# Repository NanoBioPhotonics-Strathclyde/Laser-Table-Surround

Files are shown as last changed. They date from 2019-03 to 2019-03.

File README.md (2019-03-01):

# Laser Table Surround

This project details the laser safety enclosure we have constructed for use with a 3x1.5m optical table. Wtih simple modifications it can be used for other sized tables.
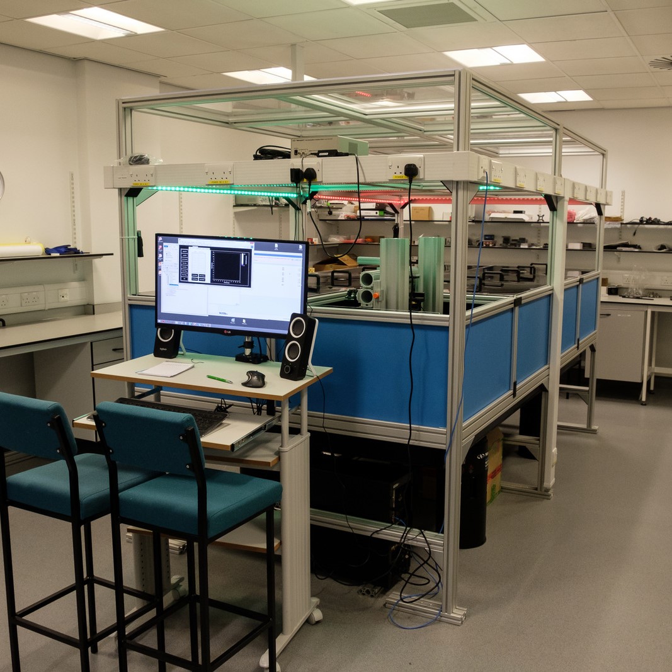
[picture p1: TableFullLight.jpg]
Laser Surround Table Fully Lit

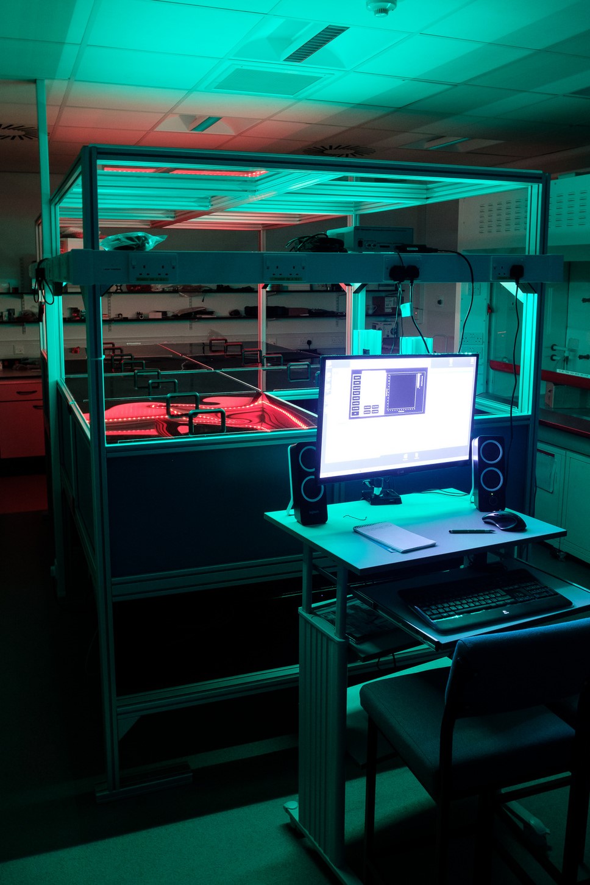
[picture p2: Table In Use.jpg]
Laser Surround in use

There were some key design considerations:
* Easily customised for other tables
* Use standard materials available from multiple suppliers when possible
* Use low cost shelving so that it can be modified quickly and replaced easily if necessary
* Stand free of the table to minimise vibration when removing top access panels
* Allow removal of side panels when necessary, but not in a way to make too easy (to prevent routine disabling of a key safety feature)
* Allow variable height from table to upper covers. This can be changed as required (though will take some disassembly).

On the last point - our optical setup means that the default height on the covers requires some lab members to use steps when accessing parts of the table. We recommend thinking about what height your sides actually need to be placed at!

The file TableSurroundConstructionHelp.pdf provides a construction schematic, and the original Sketchup design file is TableWithSurround.skp. Note that this is in multiple layers containing different classes of components. The colour coding identifies identical parts (by length or type)

We settled on aluminium extrusion for the frame. There are a number of suppliers; we used "Item 8" and the parts numbers in the full parts spreadsheet ("TableSurround Parts Sheet.ods") refer to the catalogue at:
https://www.item24.de/en/productworld/building-kit-system/item-profiles.html

The file "PanelHolderCutList.txt" gives a sample cut list to generate the required lengths from standard 2m lengths  of the profile.

We used 2mm black anodised aluminium for the side panels and sprayed the outer sides with self-priming acrylic for aesthetic purposes.

We then used 10mm clear plexiglass (any supplier) for the shelving and dark 5mm plexiglass with handles from rs for the covers. Clear plexiglass is useful for the shelving as it is strong, easily cut, and allows room light to the table when not working in the dark. The dark plexiglass for the covers was chosen as we enclose the beam paths on our table, so the covers are working to provide thermal stability and prevent room light ingress rather than as the primary safety mechanism for beams travelling vertically. Use alternative materials when this is the case.
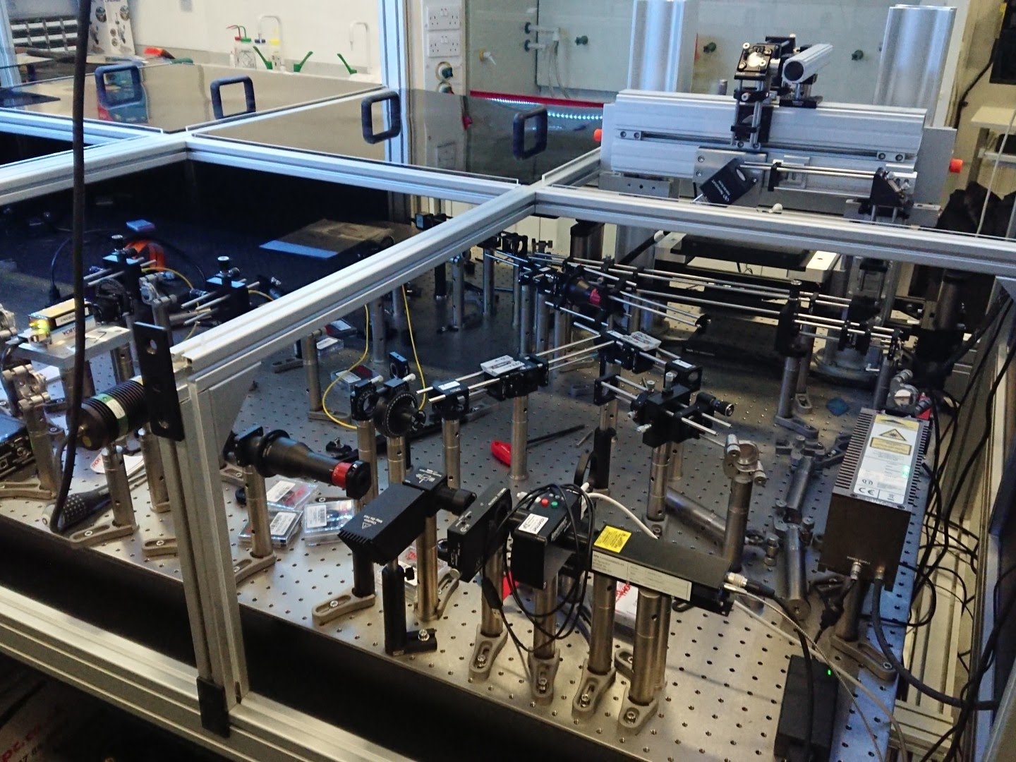
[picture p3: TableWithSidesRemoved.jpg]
Table with sides removed

The above image shows how we prevent the panels and shelves from sliding; we use small strips of  5mm plexiglass in the upper slots of the extrusion. The strips are held in place with lengths of this:
https://uk.rs-online.com/web/p/cover-strips/7675623/

We used LED lighting strips mounted under the lower shelving (they can be seen in the reflections on the covers in the picture of the table when lit up). These work very well  - they act as extended sources, so you cast little shadow when working on the table.

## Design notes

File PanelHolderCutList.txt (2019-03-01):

Cutlist — Cut list for profile panel holder pieces

Generating the following components:
  [1] ? 1590mm (x4)
  [2] ? 400mm (x24)
  [3] ? 735mm (x26)
  [4] ? 770mm (x12)
  [5] ? 805mm (x2)

The following stock board lengths are available:
  2000mm

Number after each row indicates which of the numbererd lengths above will be cut
e.g. 323 is 2xPiece[3], 1xPiece[2]
The ordering is the result of the algorithm to generate the list and does not
need to be followed for any individual cut row

Results:
2000mm board = [2] 400mm + [1] 1590mm + 1mm cut losses + 9mm excess
21
2000mm board = [2] 400mm + [1] 1590mm + 1mm cut losses + 9mm excess
21
2000mm board = [2] 400mm + [1] 1590mm + 1mm cut losses + 9mm excess
21
2000mm board = [2] 400mm + [1] 1590mm + 1mm cut losses + 9mm excess
21
2000mm board = [5] 805mm + [5] 805mm + 1mm cut losses + 389mm excess
55
2000mm board = [4] 770mm + [2] 400mm + [4] 770mm + 1.5mm cut losses + 58.5mm excess
424
2000mm board = [4] 770mm + [2] 400mm + [4] 770mm + 1.5mm cut losses + 58.5mm excess
424
2000mm board = [4] 770mm + [2] 400mm + [4] 770mm + 1.5mm cut losses + 58.5mm excess
424
2000mm board = [4] 770mm + [2] 400mm + [4] 770mm + 1.5mm cut losses + 58.5mm excess
424
2000mm board = [4] 770mm + [2] 400mm + [4] 770mm + 1.5mm cut losses + 58.5mm excess
424
2000mm board = [4] 770mm + [2] 400mm + [4] 770mm + 1.5mm cut losses + 58.5mm excess
424
2000mm board = [3] 735mm + [2] 400mm + [3] 735mm + 1.5mm cut losses + 128.5mm excess
323
2000mm board = [3] 735mm + [2] 400mm + [3] 735mm + 1.5mm cut losses + 128.5mm excess
323
2000mm board = [3] 735mm + [2] 400mm + [3] 735mm + 1.5mm cut losses + 128.5mm excess
323
2000mm board = [3] 735mm + [2] 400mm + [3] 735mm + 1.5mm cut losses + 128.5mm excess
323
2000mm board = [3] 735mm + [2] 400mm + [3] 735mm + 1.5mm cut losses + 128.5mm excess
323
2000mm board = [3] 735mm + [2] 400mm + [3] 735mm + 1.5mm cut losses + 128.5mm excess
323
2000mm board = [3] 735mm + [2] 400mm + [3] 735mm + 1.5mm cut losses + 128.5mm excess
323
2000mm board = [3] 735mm + [2] 400mm + [3] 735mm + 1.5mm cut losses + 128.5mm excess
323
2000mm board = [3] 735mm + [2] 400mm + [3] 735mm + 1.5mm cut losses + 128.5mm excess
323
2000mm board = [3] 735mm + [2] 400mm + [3] 735mm + 1.5mm cut losses + 128.5mm excess
323
2000mm board = [3] 735mm + [2] 400mm + [3] 735mm + 1.5mm cut losses + 128.5mm excess
323
2000mm board = [3] 735mm + [2] 400mm + [3] 735mm + 1.5mm cut losses + 128.5mm excess
323
2000mm board = [3] 735mm + [2] 400mm + [3] 735mm + 1.5mm cut losses + 128.5mm excess
323
2000mm board = [2] 400mm + 0.5mm cut losses + 1599.5mm excess
2

Board Count:
  25x 2000mm (Standard mm length)
Generated at http://jonathan.overholt.org/projects/cutlist

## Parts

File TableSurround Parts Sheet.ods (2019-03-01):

Part Description | Number | Comments | Part Number | Length
Fixing hardware
Angle Bracket V 8 40 Zn | 8 | Includes mounting hardware | 0.0.486.28
Angle Bracket 80x160 | 16 | This set includes mounting hardware | 0.0.436.24
Angle Bracket 80x80 | 34 | This set includes mounting hardware | 0.0.411.32
Automatic Fastening | 80 | These are individuals - get multipack? | 0.0.388.08
Flat Bracket 120x40 | 8 |  | 0.0.640.54
Flat Bracket 80x40 | 8 |  | 0.0.196.86
Rebate Profile 8Al6M5 500mm | 64 | For shelf fixing, can cut 2000mm lengths ourselves - then need 16x2m lengths | 0.0.605.21 | 500mm
Knuckle Foot | 6 | Standard, each supports 150kg | 0.0.364.68
Fastening set for flat brackets | 40 |  | 0.0.350.17
Profile panel holder sections
Cover Profile PP 1590mm | 4 | This is the Item8 part, we used RS | 0.0.422.23
Cover Profile PP 400mm | 24 |  | 0.0.422.23
Cover Profile PP 735mm | 26 |  | 0.0.422.23
Cover Profile PP 770mm | 12 |  | 0.0.422.23
Cover Profile PP 805mm | 2 |  | 0.0.422.23
Profile sections
Profile 40x40x1510 | 4 | Top shelf supports, full strength | 0.0.026.03 | 1.51m
Profile 40x40x1680 | 2 | Full width supports for top panels, should be full strength | 0.0.026.03 | 1.68m
Profile 40x40x400 | 6 | Vertical support for top panel cross members, full strength | 0.0.026.03 | 0.4m
Profile 40x40x735 | 10 | Top panel supports, can be light | 0.0.026.33 | 0.735m
Profile 40x40x760 | 8 | Shelf support, should be full strength | 0.0.026.03 | 0.76m
Profile 40x40x780 | 4 | Top panel support, can be light | 0.0.026.33 | 0.78m
Profile 40x40x815 | 2 | Top panel support, can be light | 0.0.026.33 | 0.815m
Profile 80x40x1510 | 12 | Longitudinal tie members, full strength | 0.0.026.04 | 1.51m
Profile 80x40x1600 | 12 | Cross tie members, should be full strength | 0.0.026.04 | 1.6m
Profile 80x40x2100 | 6 | Main frame verticals, use full strength | 0.0.026.04 | 2.1m
Profile 80x40x3260 | 1 | Longtiudinal tie bar, can be light | 0.0.026.34 | 3.26m
Side and top panels
Side Panel 750x415x2 | 8 | Anodised Alu - thickness can be smaller
End Panel 795x415x2mm | 4 | Anodised Alu - thickness can be smaller
Panel Spacer 20x5x730mm | 24 | Can be any suitable perspex/plastic - does not need to be laser safe |  | 730mm
Top Panel 805x805x5mm | 4 | Can be black perspex
Top Panel 805x760x5mm | 4 | Can be black perspex

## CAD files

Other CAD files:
TableWithSurround.skp

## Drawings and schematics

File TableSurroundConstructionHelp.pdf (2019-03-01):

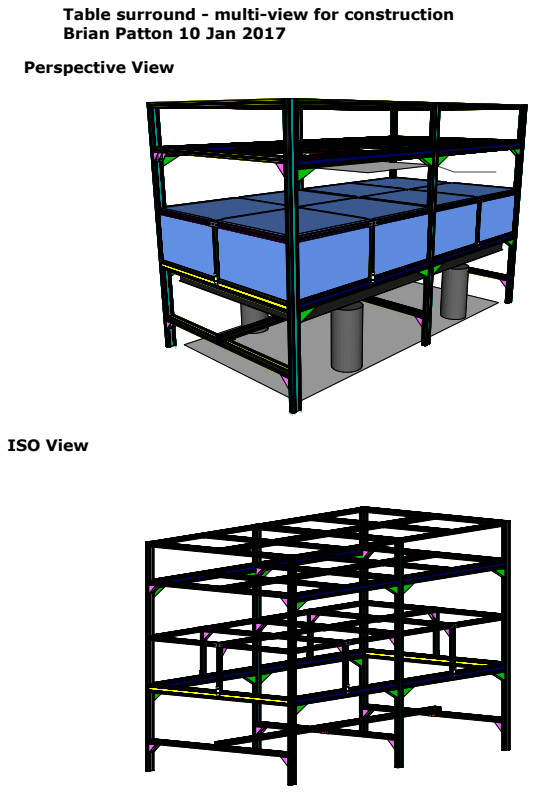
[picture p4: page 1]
Perspective View; ISO View

Table surround - multi-view for construction
Brian Patton 10 Jan 2017

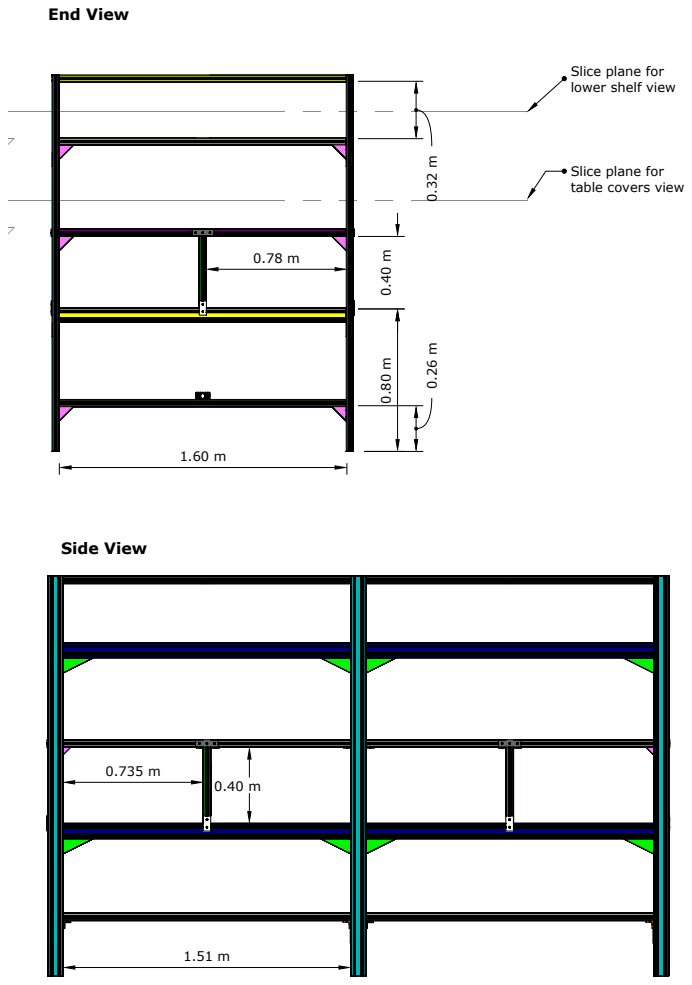
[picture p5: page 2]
End View; Side View

Slice plane for
lower shelf view

table covers view

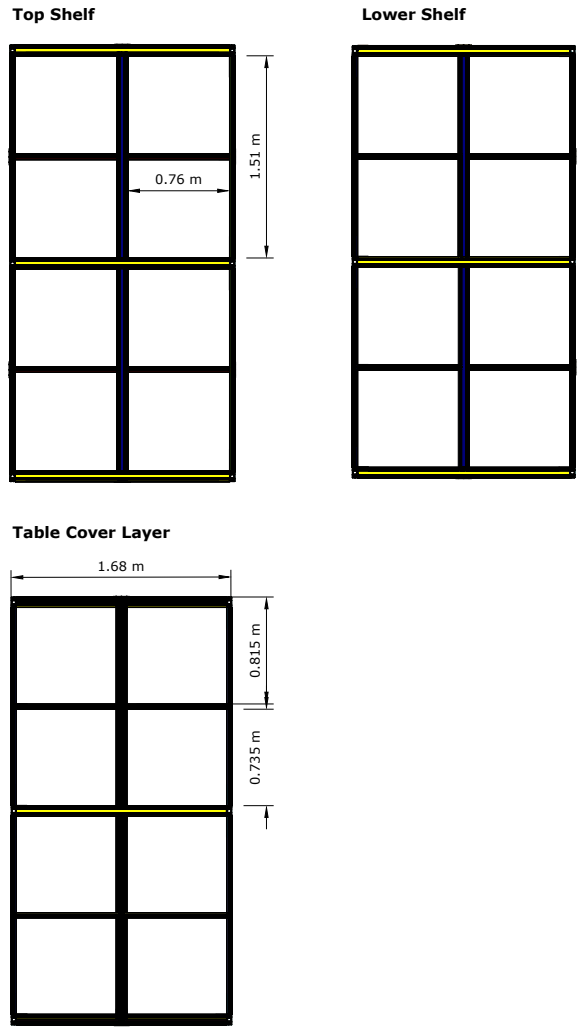
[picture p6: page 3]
Top Shelf; Lower Shelf

Table Cover Layer
